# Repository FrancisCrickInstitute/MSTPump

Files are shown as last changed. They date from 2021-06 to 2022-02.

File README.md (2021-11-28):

# MSTPump
Open source syringe pump based on the Teensy 3.2 development board and the TeensyStep library.
The electronics board needed to replicate the pump is available on this other repository:
https://github.com/FrancisCrickInstitute/StepperController

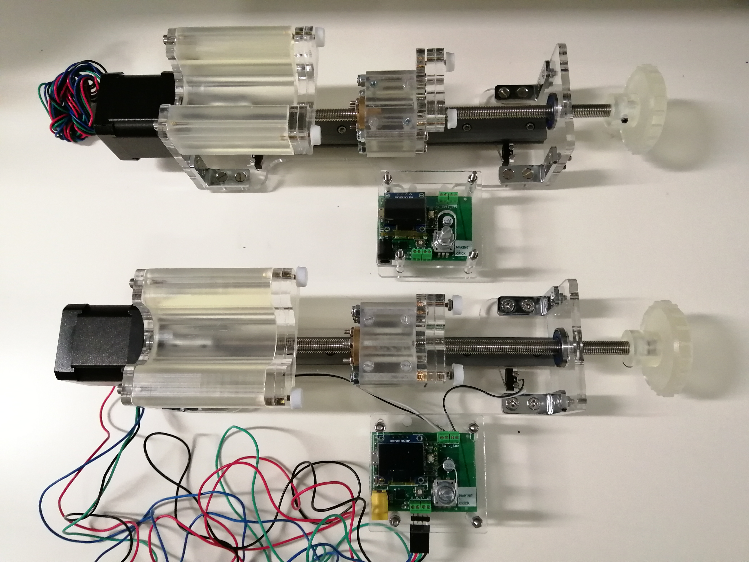
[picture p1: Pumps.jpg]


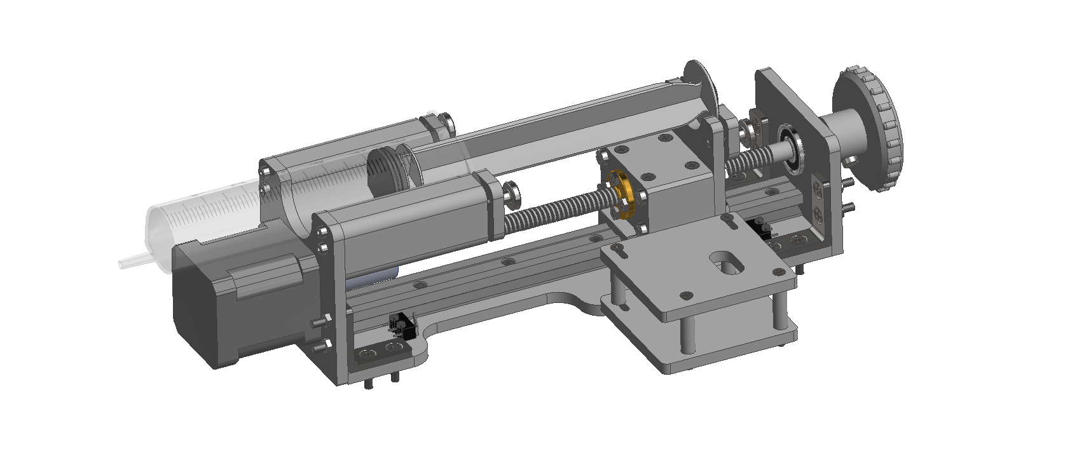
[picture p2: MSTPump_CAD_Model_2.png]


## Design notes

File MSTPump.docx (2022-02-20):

The MSTPump: Open source syringe pump

Xavier Cano-Ferrer, George Konstantinou & Albane Imbert

The Making STP, The Francis Crick Institute

One of the most common devices used in microfluidics flow rate controlled experiments are the syringe pumps. These types of pumps are able to control the fluid flow rate by controlling accurately a stepper motor attached to a lead screw which transfers the rotational movement of the motor shaft into a linear translation of a platform that slides across low friction element rail or slide bar. In this article we present a teensy 3.2 development board based robust and precise syringe pump that can be build using digital manufacturing techniques such as laser cutting and 3D printing.

Introduction

Over the last decade, several research labs, individual researchers or even makers have developed rapid manufactured syringe pumps. This list includes the model from the from the Janelia research campus [1], Jakob Voigts design [2], the Poseidon syringe pump system developed on California Institute of Technology [3], the Open-source syringe pump from the Michigan Tech's Open Sustainability Technology Lab [4], the 3D Printed Syringe Pump Rack by Aldricnegrier [5] or the DIY Syringe Pump by Naroom [6]. The MSTPump takes the advantage of using the highly reliable and precise stepper motor control provided by the teensystep.h library [7] to achieve high performance device.

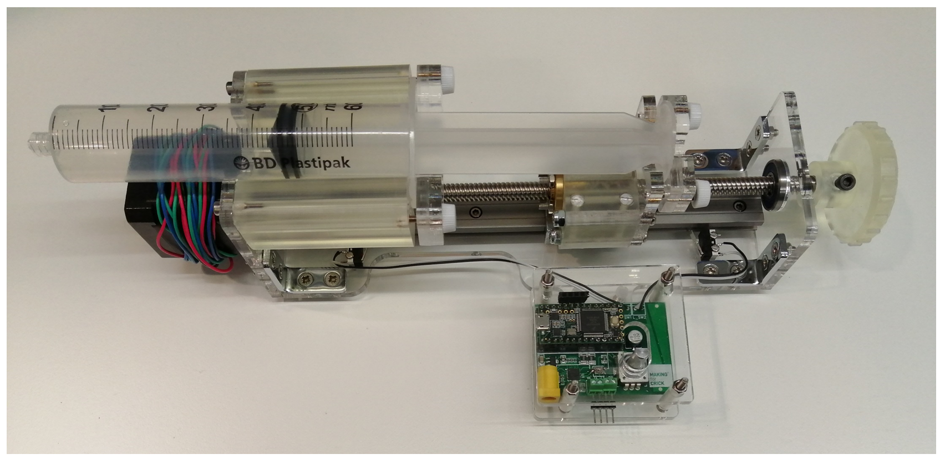
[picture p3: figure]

Figure 1: Syringe pump prototype.

Device description

The syringe pump has been conceived to operate with a BD Plastipak 60 mL syringe and therefore a 26.72 mm internal diameter [8]. That dimension has been used to calculate the area of the fluid that is displaced every step, being this one 560.74 mm^2. The resolution is changeable by defining the state of MS1, MS2 or MS3 to HIGH or LOW. The resolution at which currently the device operates is 3200 pulse/revolution. The lead size depends on the desired application and can be changed to 1,2,4 or 8 mm on the program the default is 1 mm. The resolution expressed in minimum volume that can be ejected depends on the selected and it ranges from 1.40 to 0.18 mm^3 for 1 and 8 mm leads respectively. The pump firmware has two main functions that convert the desired volume (µL) and flow rate (µL/s) into rotational displacement (steps) and rotational speed (steps/s) at a given acceleration. The default acceleration is set to 5000 steps/s^2.

The volumetric resolution ( V_r ) is calculated as the minimum volume that can be delivered with a certain lead ( l ), syringe cross sectional area ( A ) and stepping resolution ( S_r ).

V_r =(l [mm])/(S_r [step])A[mm^2 ]=0.18[(mm^3)/(step)]

The function which returns the number of steps ( S ) by a given volume ( V ) in µL:

S=(V [mm^3 ])/(V_r [(mm^3)/(step)])=[step]

The function which returns the number of steps per second ( S ) by a given flow rate ( V ) in µL/min:

S=(V [mm^3 ])/(60 [s])1/(V_r [(mm^3)/(step)])=[(step)/s]

Experimental methods

The precision and repeatability of the two pumps has been evaluated with two different lead screws, with coarse (8mm) and fine (1mm) leads respectively. In order to precisely measure the quantity of water ejected by the pump, ten 1.5 mL falcon tubes were marked with a number and weighted three times with a precision scale (Sartorius Analytic A 200S), the average of the three measurements was taken. The syringe pump was programmed to eject 1000 µL of water at three different flow rates: 1, 10 and 100 mL/min. Each of the ten previously mention tubes were filled with this volume of water. The procedure was performed for the 1 and 8 mm leads.

Results and discussion

The experimental results with the lead screw with 8 mm lead (Four start) have shown an average volume of 982±15 µL with a relative error of 1.78% from the desired volume of 1000 µL (Figure 2).

Figure 2: Ejected volumes at three different flow rates (1, 10 and 100 mL/min with an 8 mm lead screw (N = 10).

In the case of the 1 mm lead screw the average volume has been 977±32 µL with a relative error of 2.25% from the desired volume of 1000 µL (Figure 3).

Figure 3: Ejected volumes at three different flow rates (1, 10 and 100 mL/min with a 1 mm lead screw (N = 10).

The Pump shows a better precision and repeatability with the 8 mm lead screw. On the other hand, with the 8mm lead it is not possible to achieve flow rate regimes lower than 86.4 µL/min. On the other hand, with the 1 mm lead screw, a wider range of flow rates can be achieved precisely, from 10.8 µL/min to 86.4 mL/min and even higher flow rates making it suitable for the microfluidic scale but also for millilitre scale experiments. The high resolution and small volume enable scientists to perform experiments of long duration (almost 4 days) with small flow rates (10.5 uL/min).

# References

[1] | K. lab, "https://karpova-lab.github.io/syringe-pump/index.html," [Online].
[2] | J. Voigts, "http://jvoigts.scripts.mit.edu/blog/low-cost-syringe-pump/," [Online].
[3] | A. S. Booeshaghi, E. d. V. Beltrame, D. Bannon, J. Gehring and L. Pachter, "Principles of open source bioinstrumentation applied to the poseidon syringe pump system," Scientific Reports, vol. 9, no. 12385, 2019.
[4] | M. T. O. S. T. Lab, "https://www.appropedia.org/Open-source_syringe_pump," [Online].
[5] | "https://www.instructables.com/3D-Printed-Syringe-Pump-Rack/," [Online].
[6] | "https://hackaday.com/2017/02/26/diy-syringe-pump-saves-big-bucks-for-hackers-lab/," [Online].
[7] | Luni64, "https://luni64.github.io/TeensyStep/," [Online].
[8] | "https://www.chemyx.com/support/knowledge-base/syringe-library/bd-plastic-syringe-minimum-maximum-flow-rates/," [Online].

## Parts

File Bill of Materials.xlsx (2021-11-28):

Component | Units | Manufacturer | Reference | Cost £ | Option 2
Rail | 1 | RS Components | https://uk.rs-online.com/web/p/linear-guides-rails/4885079/ | 17.16
Carriage | 1 | RS Components | https://uk.rs-online.com/web/p/guide-blocks-guide-carriages/4884997/?searchHistory=%7B%22enabled%22%3Atrue%7D | 20.58
AC/DC Converter | 1 | RS Components | 12V, 1.5A (Barrel jack 2 mm connector)
Micro Switch | 2 | Amazon | https://www.amazon.co.uk/gp/product/B07YDFH7H3/ref=ppx_yo_dt_b_asin_title_o07_s02?ie=UTF8&psc=1 | 2.99
M3.5 Nut | 16 | Amazon | https://www.amazon.co.uk/gp/product/B07YCBWWXX/ref=ppx_yo_dt_b_asin_title_o07_s00?ie=UTF8&psc=1 | 5.49
M3.5 Screw | 16 | Amazon | https://www.amazon.co.uk/gp/product/B07RX1PZYK/ref=ppx_yo_dt_b_asin_title_o07_s01?ie=UTF8&psc=1 | 5.49
OLED Display | 1 | Amazon | https://www.amazon.co.uk/gp/product/B01L9GC470/ref=ppx_yo_dt_b_asin_title_o01_s00?ie=UTF8&psc=1 | 4.99
Lead screw + nut (1mm) | 1 | Amazon | https://www.amazon.co.uk/gp/product/B08M3NTDGJ/ref=ppx_yo_dt_b_asin_title_o02_s00?ie=UTF8&psc=1 | 13.14
Lead screw + nut (8mm) | 1 | Amazon | https://www.amazon.co.uk/gp/product/B07P6HQMHT/ref=ppx_yo_dt_b_asin_title_o03_s00?ie=UTF8&psc=1 | 14.99
Coupler | 1 | Amazon | https://www.amazon.co.uk/gp/product/B0783QQMKP/ref=ppx_yo_dt_b_asin_title_o03_s00?ie=UTF8&psc=1 | 8.99
Nema 17 stepper motor | 1 | Amazon | https://www.amazon.co.uk/gp/product/B077YMHH8P/ref=ppx_yo_dt_b_asin_title_o06_s00?ie=UTF8&psc=1 | 25.55 | https://www.amazon.co.uk/STEPPERONLINE-Stepper-Motor-Connector-Printer/dp/B07FMBXF3T?s=industrial
Potentiometer 10k | 1
Bracket | 4 | RS Components | https://uk.rs-online.com/web/p/enclosure-mounting-brackets/7491686/ | 24.43
M2 screw | 4 | -
M2 nut | 4 | -
M3 screw | 24 | -
M3 thumb screw | 10 | -
M3 threaded insert | 6 | -
M3 nut | 14 | -
M4 screw | 4 | -
M4 nut | 4 | -
Bearing | 1 | Amazon | https://www.amazon.co.uk/CODIRATO-Skateboard-Bearings-Longboard-Skateboards/dp/B07TB6Y9ZK | 7.59
Nema 17 spacer | 1 | https://github.com/FrancisCrickInstitute/MSTPump | 3D printed
Electronics spacer | 1 |  | 3D printed
Manual adjuster | 1 |  | 3D printed
Cart | 1 |  | 3D printed
Motor holder | 1 |  | Laser cut
Base | 1 |  | Laser cut
Syringe front holder | 2 |  | Laser cut
Syringe back holder | 2 |  | Laser cut
Syringe back holder 2 | 1 |  | Laser cut
Bearing holder | 1 |  | Laser cut
Electronics base | 1 |  | Laser cut
Electronics cover | 1 |  | Laser cut
Assembled PCB | 1 | https://github.com/FrancisCrickInstitute/StepperController | Gerber file (JCB PCB)
Teensy 3.2 | 1 | Digikey | https://www.digikey.co.uk/reference-designs/en/open-source-mcu-platforms/open-source-mcu-platforms/2548?productid= | 20.29
2.54 mm Female pin header | 1 | -
 |  |  |  | 171.68

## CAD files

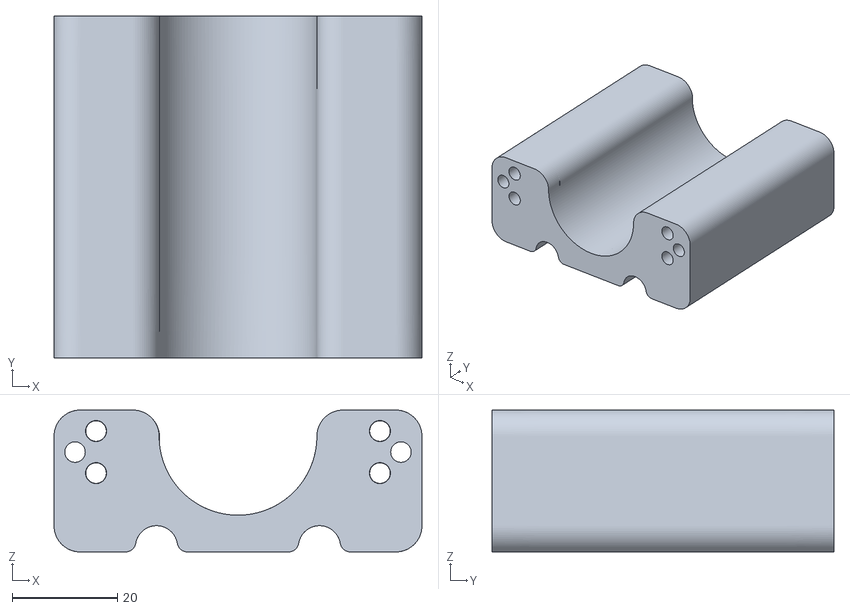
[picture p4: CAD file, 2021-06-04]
STL files/Nema 17 vertical suport spacer.stl
70.0 x 65.0 x 27.0

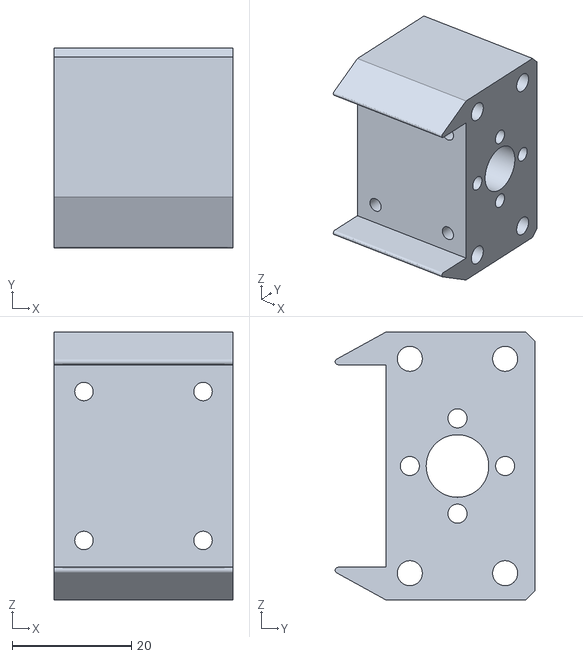
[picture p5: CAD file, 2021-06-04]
STL files/Cart 2.stl
30.0 x 33.6 x 45.0

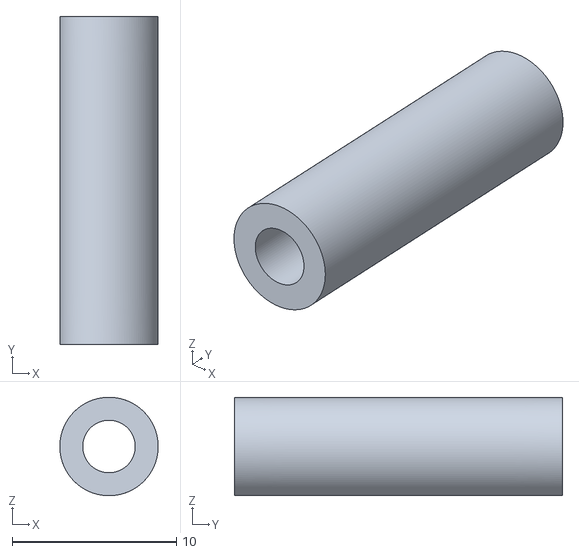
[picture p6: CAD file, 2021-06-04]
STL files/Electronics spacer.stl
6.00 x 20.0 x 6.00

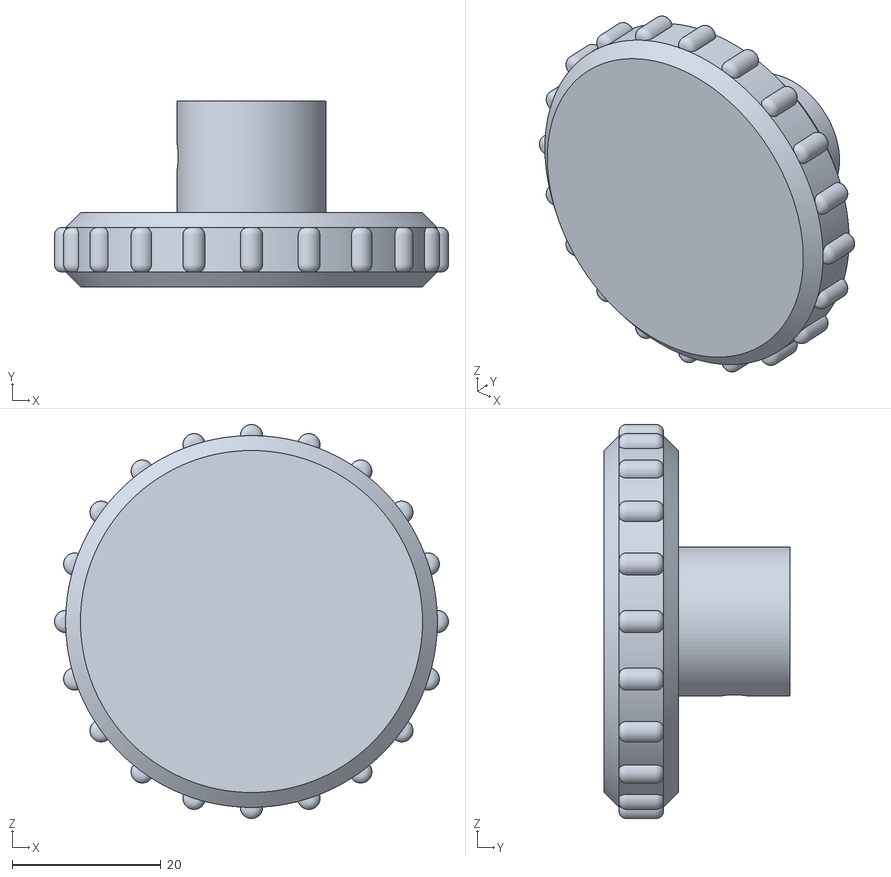
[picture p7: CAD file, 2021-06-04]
STL files/Lead screw manual adjuster.stl
53.0 x 25.0 x 53.0

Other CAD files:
Laser cut files/Motor holder.dwg
Laser cut files/Electronics base.dwg
Laser cut files/Syringe holder part 2.dwg
Laser cut files/Bearing holder.dwg
Laser cut files/Base.dwg
Laser cut files/Syringe holder.dwg
Laser cut files/Syringe holder part 3.dwg
Laser cut files/Electromics cover.dwg

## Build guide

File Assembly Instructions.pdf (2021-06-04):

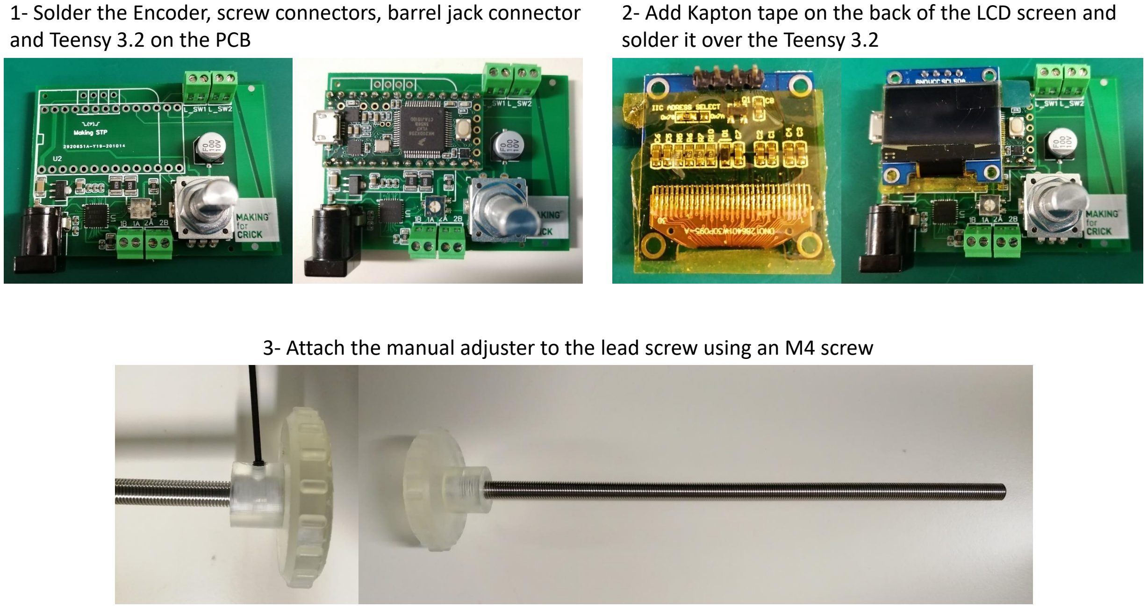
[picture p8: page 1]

1- Solder the Encoder, screw connectors, barrel jack connector and Teensy 3.2 on the PCB

2- Add Kapton tape on the back of the LCD screen and solder it over the Teensy 3.2

3- Attach the manual adjuster to the lead screw using an M4 screw

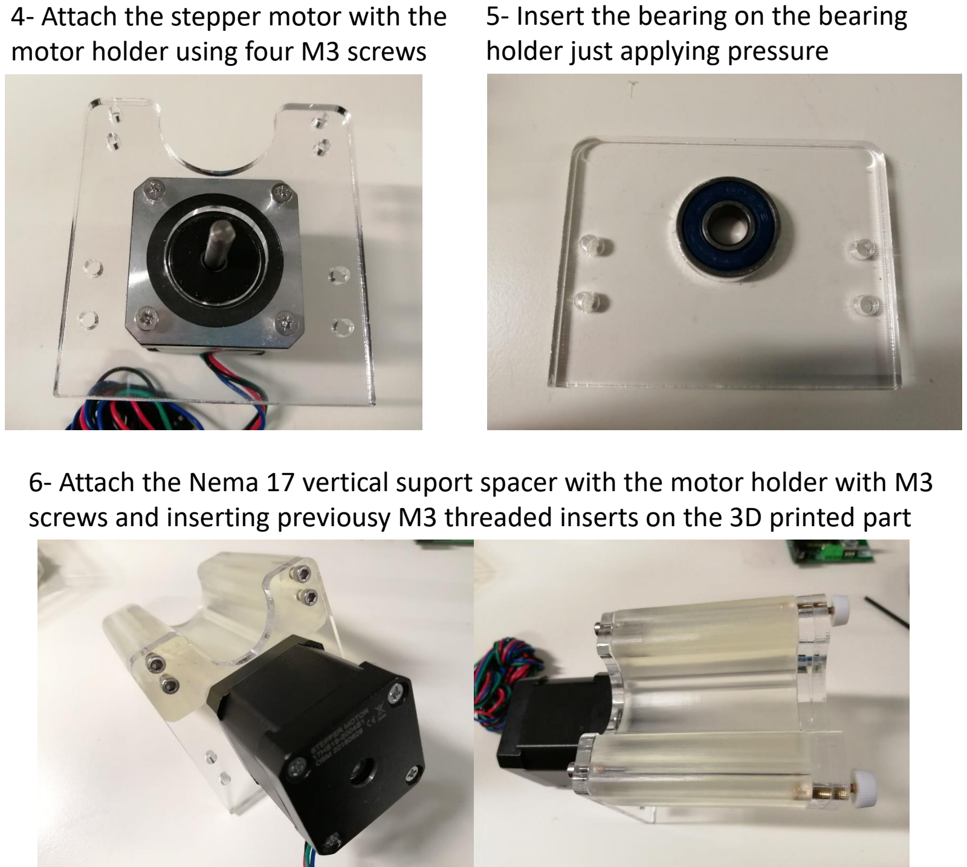
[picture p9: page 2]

4- Attach the stepper motor with the motor holder using four M3 screws

5- Insert the bearing on the bearing holder just applying pressure

6- Attach the Nema 17 vertical suport spacer with the motor holder with M3 screws and inserting previousy M3 threaded inserts on the 3D printed part

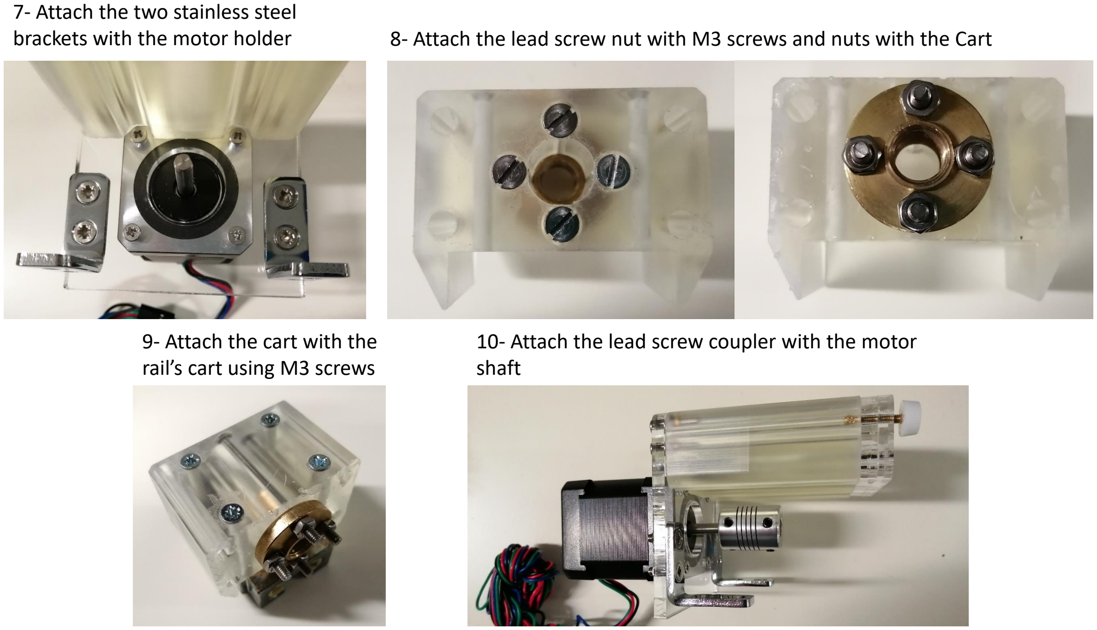
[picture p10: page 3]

7- Attach the two stainless steel
brackets with the motor holder | 8- Attach the lead screw nut with M3 screws and nuts with the Cart

10- Attach the lead screw coupler with the motor shaft

9- Attach the cart with the rail’s cart using M3 screws

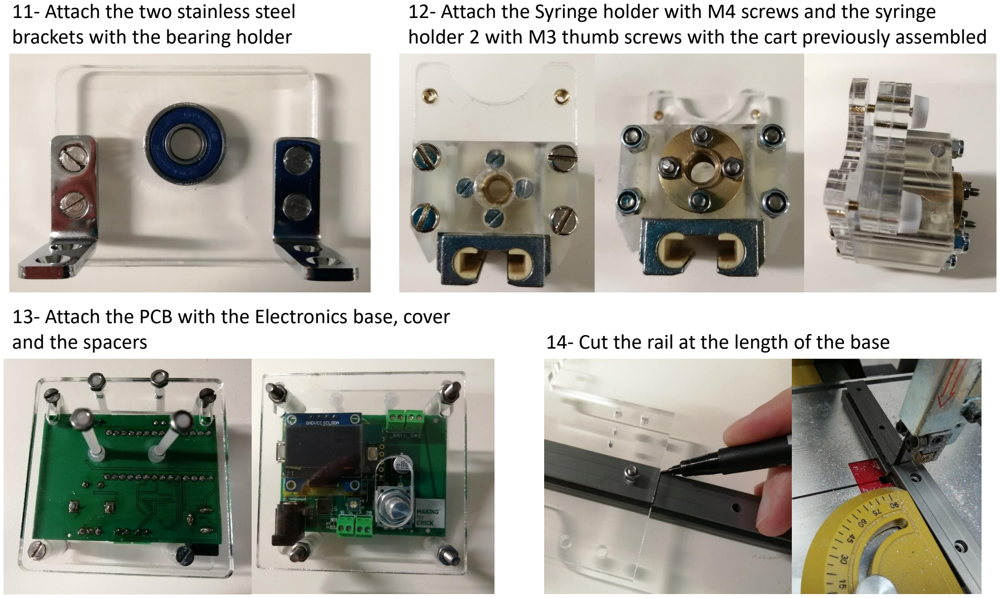
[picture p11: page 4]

11- Attach the two stainless steel brackets with the bearing holder

12- Attach the Syringe holder with M4 screws and the syringe holder 2 with M3 thumb screws with the cart previously assembled

13- Attach the PCB with the Electronics base, cover
and the spacers | 14- Cut the rail at the length of the base

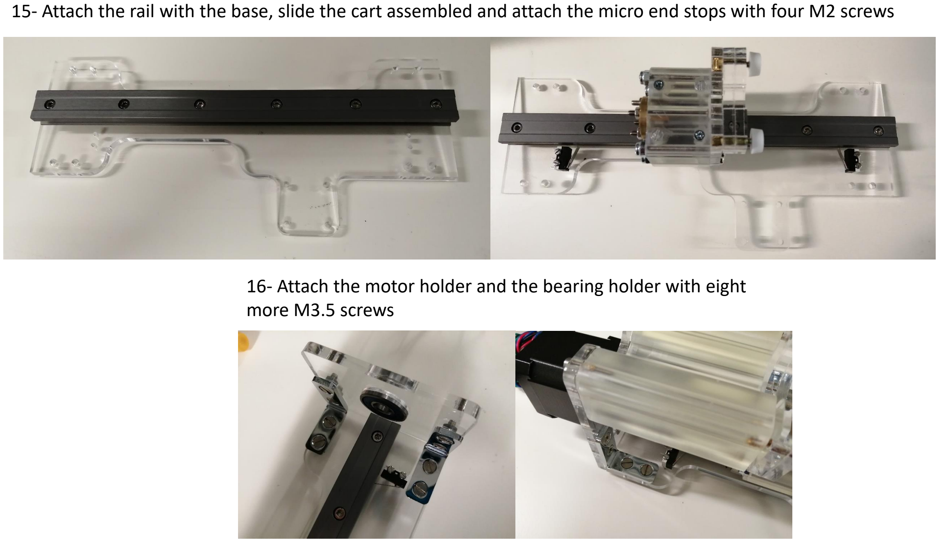
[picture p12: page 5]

15- Attach the rail with the base, slide the cart assembled and attach the micro end stops with four M2 screws

16- Attach the motor holder and the bearing holder with eight more M3.5 screws

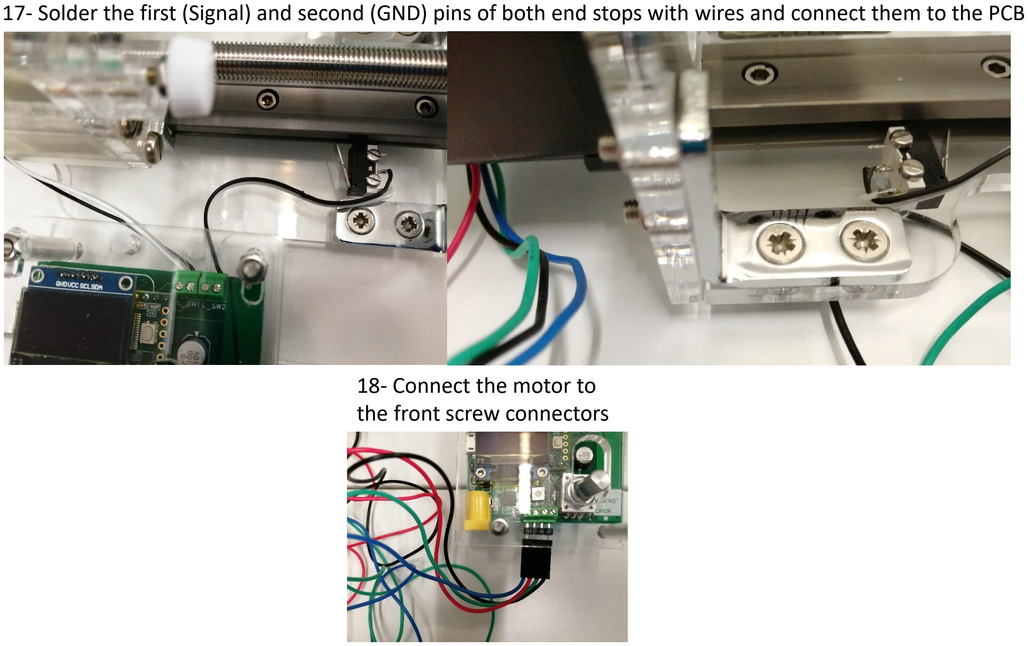
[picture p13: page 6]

17- Solder the first (Signal) and second (GND) pins of both end stops with wires and connect them to the PCB

18- Connect the motor to
the front screw connectors

19- Upload the Code: Syringe_pump_flow_rate_push.ino and connect the 12V power supply to verify that everything is working fine

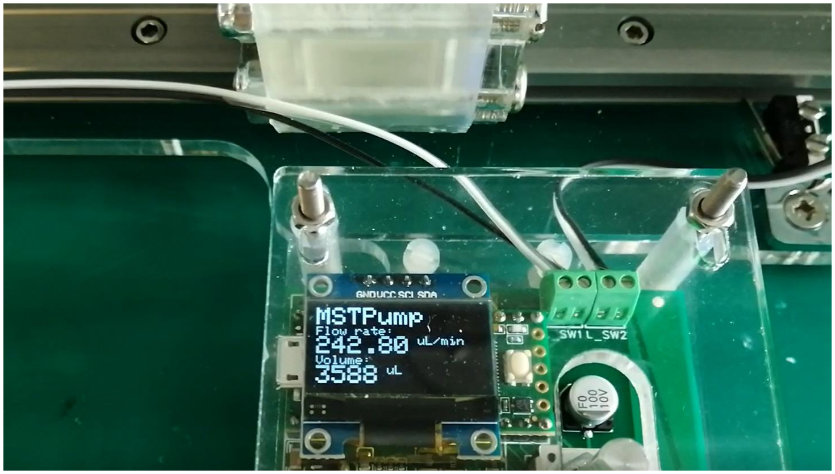
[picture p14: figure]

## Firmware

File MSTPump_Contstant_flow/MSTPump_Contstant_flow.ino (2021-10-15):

#include "TeensyStep.h"
#include <Encoder.h>
#include <Wire.h>
#include <Adafruit_GFX.h>
#include <Adafruit_SSD1306.h>
#include <Bounce.h>

Encoder knob(10, 11);
const int encoder_SW = 12;
Bounce pushbutton = Bounce(encoder_SW, 10);  // 10 ms debounce
bool state = 0;

Stepper pump(7, 6);       // STEP pin: 7, DIR pin: 6  // The stepper class encapsulates the physical properties of a stepper motor like pin numbers of the STEP and DIR signals, speed and acceleration of the motor.
//StepControl step_controller;    // The StepControl class is used to synchronously move up to 10 motors to their target positions.
RotateControl rotate_controller; // The RotateControl class is used to synchronously rotate up to 10 motors.
int speed_ = 0;

//Fluid global constants
//const int lead_size = 8; // lead size (8mm)
const int lead_size = 1; // lead size (1mm)
const float steps_rev = 3200; // Stepper resolution at 1/16 steps per revolution
const float syringe_area = 560;// Syringe cross section area(560 mm^2 Hardvare apparatus).(549.88 Datasheet)
float linear_resolution = (lead_size/steps_rev)*syringe_area; //uL/step or mm^3/step

float Volume;
float flow_rate;
int steps;
int steps_s;

#define SCREEN_WIDTH 128 // OLED display width, in pixels
#define SCREEN_HEIGHT 64 // OLED display height, in pixels

// Declaration for an SSD1306 display connected to I2C (SDA, SCL pins)
#define OLED_RESET     -1 // Reset pin # (or -1 if sharing Arduino reset pin)

Adafruit_SSD1306 display(SCREEN_WIDTH, SCREEN_HEIGHT, &Wire, OLED_RESET);

const int MS1 = 3;
const int MS2 = 4;
const int MS3 = 5;
const int Enable = 2;

// limit switches
const int LSW1 = 15;
const int LSW2 = 14;

Bounce limitswitch_back = Bounce(LSW2,10);
Bounce limitswitch_front = Bounce(LSW1,10);

//Direction
bool dir = true;

void setup()
{
  pinMode(MS1, OUTPUT);    // set the MS1, MS2, MS3 and Enable as an outputs
  pinMode(MS2, OUTPUT);
  pinMode(MS3, OUTPUT);
  pinMode(Enable, OUTPUT);

  digitalWrite(MS1, HIGH); // sets the digital pin MS1, MS2, MS3 to HIGH
  digitalWrite(MS2, HIGH);
  digitalWrite(MS3, HIGH);
  digitalWrite(Enable, HIGH); // set the enable to HIGH
  
  // Set the motor max acceleration
  pump.setAcceleration(500)   // stp/s^2
      .setInverseRotation(true);
  
  pinMode(LSW1, INPUT_PULLUP);
  pinMode(LSW2, INPUT_PULLUP);
  pinMode(encoder_SW, INPUT_PULLUP);
  
  Serial.begin(115200);
  
  display.begin(SSD1306_SWITCHCAPVCC, 0x3C);
  delay(1000); 
  display.clearDisplay();

}

void loop() 
{ 
  
  read_pushbutton();
  
  OLED_display();
  
  flow_rate =(knob.read()/2)*linear_resolution*60;
      
  steps_s = get_speed(flow_rate);

  digitalWrite(Enable, HIGH);
  
  rotate_controller.stop();
  
  while (digitalRead(LSW2)==HIGH && digitalRead(LSW1)==HIGH && state == HIGH)
  {
      digitalWrite(Enable, LOW);

      read_pushbutton();    
      
      flow_rate =(knob.read()/2)*linear_resolution*60;
 
      steps_s = get_speed(flow_rate);
      Volume = get_volume(pump.getPosition());
  
      pump.setMaxSpeed(steps_s)
      .setInverseRotation(dir);
      rotate_controller.rotateAsync(pump);
  
      OLED_display();


  }
  

}

int get_speed(float flow_rate)
{
  float uL_s = flow_rate/60;
  int steps_s;
  steps_s = uL_s*(1/linear_resolution);
  return steps_s;
}

int get_steps(int Volume)
{
  int linear_displacement = Volume/linear_resolution;
  return linear_displacement;
}

float get_volume(int steps)
{
  int Volume = steps*linear_resolution;
  return Volume;
}

void OLED_display()
{   
    display.clearDisplay();
    display.setTextColor(WHITE);        // Draw white text
    display.setCursor(0, 0);
    display.setTextSize(2);
    display.print(F("MSTPump"));
    display.setTextSize(1);
    display.println();
    display.println();
    display.print(F("Flow rate selected:"));
    display.println();
    display.setTextSize(1);
    display.print((knob.read()/2)*linear_resolution*60);
    display.setTextSize(1);
    display.println  (F(" uL/min"));
    display.print(F("Flow rate dispensed:"));
    display.println();
    display.print(rotate_controller.getCurrentSpeed()*linear_resolution*60); 
    display.println  (F(" uL/min"));
    display.setTextSize(1);
    display.print(F("Volume:"));
    display.print(int(Volume));
    display.setTextSize(1);
    display.println(F(" uL"));
    display.display(); 
}

void read_pushbutton()
{
    if (pushbutton.update()) 
    {
      if (pushbutton.fallingEdge()) 
      {
        state = !state;
      }
    } 
}

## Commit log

2021-06-04 Update MSTPump assembly.stp
2021-11-25 Bill of materials update
    [BOM.xlsx, Bill of Materials.xlsx]
2021-11-28 Update Bill of Materials.xlsx
    [Bill of Materials.xlsx]
